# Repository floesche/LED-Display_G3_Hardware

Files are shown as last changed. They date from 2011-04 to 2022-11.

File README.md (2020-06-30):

# Modular display system, Generation 3 Hardware

This repository contains information related to the 3rd generation of modular
displays, as described in:

Reiser, M.B. and Dickinson, M.H., 2008. A modular display system for insect behavioral neuroscience. *Journal of Neuroscience Methods, 167*(2), pp.127-139 [doi:10.1016/j.jneumeth.2007.07.019](https://doi.org/10.1016/j.jneumeth.2007.07.019)

More information is available in the [Wiki](https://github.com/reiserlab/Panel-G3-Hardware/wiki)

This repository used to live on https://bitbucket.org/mreiser before June 2020.

## related repositories

- (this repository) [Panel Generation 3 Hardware](https://github.com/reiserlab/Panel-G3-Hardware)
- [Panel Generation 3 Software](https://github.com/reiserlab/Panel-G3-Software)
- [Panel Generation 4 Tools](https://github.com/JaneliaSciComp/G4_Display_Tools)

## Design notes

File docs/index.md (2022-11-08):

---
title: Hardware
parent: Generation 3
has_children: true
has_toc: false
nav_order: 1
---

# Home

These pages document the hardware details of the Generation 3 controller project (PDC 3.0, released April 2011). The documentation for the version 2 of the project is archived [here]({{site.baseurl}}/G2/).

What is new in PDC 3.0?

- Xmega controller
- 4 I²C busses
- improved ADC and DCA components

# At a Glance

1. The flight arena consists of a circular array of 8×8 dot matrix displays of LEDs with additional electronics to drive the display.
1. The data acquisition module is often called the NI-DAQ (National Instruments Data Acquisition Device). In this case, the NI-DAQ is a [NI USB-6229 BNC](https://www.ni.com/documentation/en/multifunction-io-device/latest/usb-6229/pinout-bnc/) Multifunction DAQ. This model has 16 analog inputs, 4 analog outputs, 8 DIOs and 2 user defined BNC terminals—more information about this device is available at <http://sine.ni.com/nips/cds/view/p/lang/en/nid/203866>.
1. The controller is a microprocessor circuit custom designed to operate the flight arena. The controller communicates with a PC through a serial port and to the panels using a rapid serial interface.
1. The wingbeat analyzer measures the frequency and amplitude of the fly wing stroke. It also computes the sum and difference of the amplitudes of the left and right wings. This device is custom built by JFI Electronics at the University of Chicago.
1. The PC is used to display patterns on the flight arena and record data through the NI-DAQ. The PC must be capable of running Matlab as well as a data acquisition program such as [AxoScope](https://www.moleculardevices.com/products/axon-patch-clamp-system/acquisition-and-analysis-software/pclamp-software-suite) or [Spikehound](https://sourceforge.net/projects/spikehound/). It must have at least one USB and one serial port.
1. An oscilloscope with three input channels and an external trigger will suffice.

# Required parts

The following is a brief list of the parts needed for a functional setup.

## Data Processing & Acquisition

1. Arena Controller -  (URL/controller details neeeded)
1. Wingbeat Analyzer (WBA) - [JFI Electronics Laboratory](https://jfi.uchicago.edu/), University of Chicago.
1. Data Acquisition Module -  [National Instruments Data Acquisition PCI-6221 Board (NI-DAQ)](http://sine.ni.com/nips/cds/view/p/lang/en/nid/14132)
1. Oscilloscope - [Tektronix TDS 2024B](https://www.tek.com/oscilloscope/tds2000-digital-storage-oscilloscope)
1. PC - Any PC capable of running matlab, a data acquisition program, and handling the card drivers for the NI-DAQ. - Our setup uses Dell Precision T5500
1. Cables - BNC, BNC-Banana adaptors, BNC T splitters, FireWire, USB A-B

## Flight Arena & Peripherals

(See [Arenas Page](g3_arenas.md) for assembly information)

1. [LED Display Panels](assets/green-panels_BM-10288MD.pdf)
1. Arena Boards - (needed)
1. IR Sensor/Cover - (needed)
1. IR Diode - (needed)
1. Camera - Point Gray Research [Firefly](http://www.ptgrey.com/products/fireflymv/fireflymv_usb_firewire_cmos_camera.asp)
1. Stage - [Thorlabs](http://www.thorlabs.com) components
1. Enclosure - Any material capable of covering the arena and preventing light from entering.
1. SDHC/CF Card - Such as from [Transcend](http://ec.transcendusa.com/product/product_memory.asp?Cid=92)

## Software

1. [MATLAB](http://www.mathworks.com/products/matlab/)
1. Data Acquisition - Such as [Spikehound](https://sourceforge.net/projects/spikehound/) or the Matlab Data Acquisition Toolbox

## Optional

1. Speakers - To hear the WBA
1. 80mm PC Case Fan - To encourage fly flight
1. Thermometer - For temperature sensitive experiments/consistency

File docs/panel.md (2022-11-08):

---
title: Panel
parent: Hardware
grand_parent: Generation 3
nav_order: 1
---

# Panel

The Generation 3 Modular LED Display uses the same panels as [Generation 2]({{site.baseurl}}/G2/). [See there]({{site.baseurl}}/Generation%202/Panels/docs/) for more information.

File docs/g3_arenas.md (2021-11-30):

---
title: Arenas
parent: Hardware
grand_parent: Generation 3
nav_order: 5
---

# Generation 3 Arena

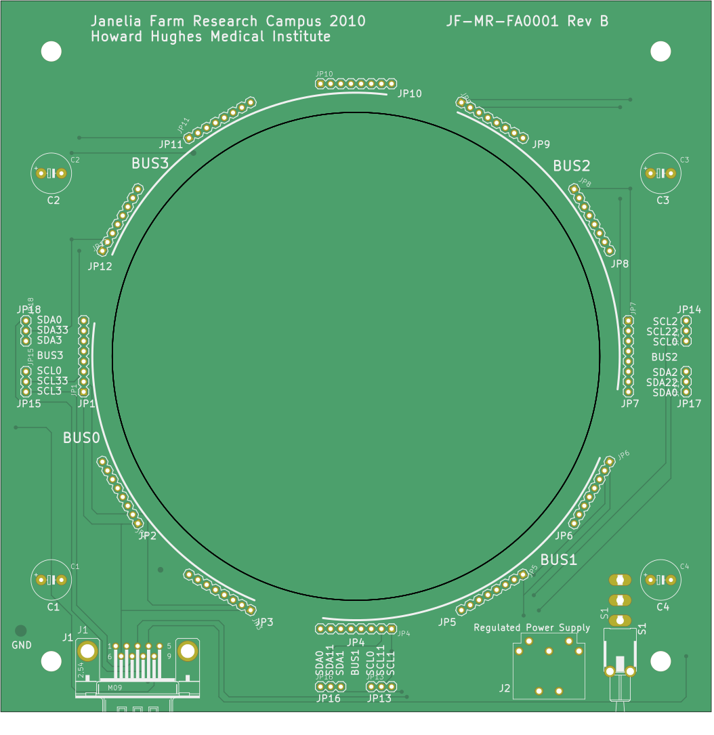
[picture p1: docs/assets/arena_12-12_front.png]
Arena 12-12 PCB front view

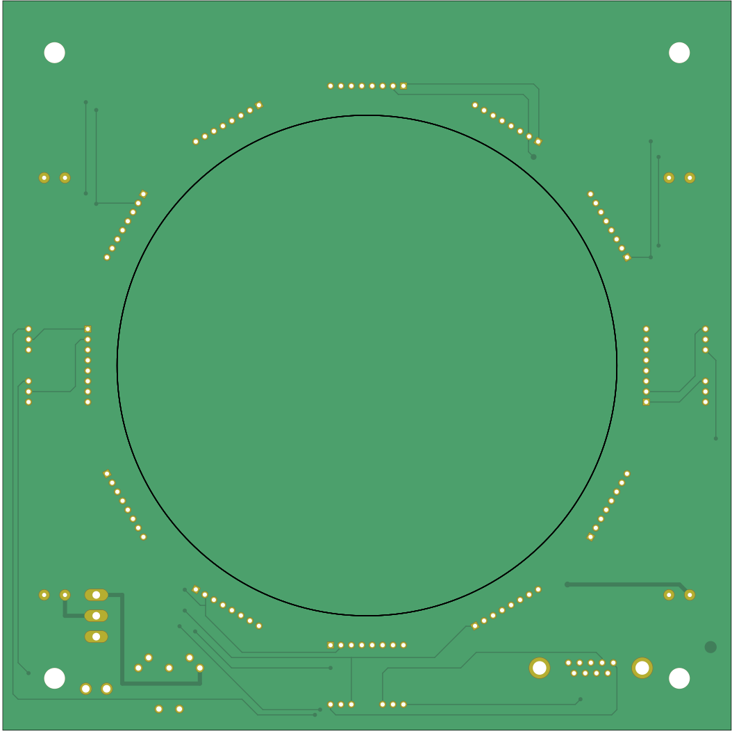
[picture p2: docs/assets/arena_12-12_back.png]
Arena 12-12 PCB back view


An arena board organizes panels in a geometry and provides structural integrity to the whole setup. Different shapes of cylindrical arenas have been built. We use a naming scheme based on their number of panel columns available and the virtual ones forming a full circle. A 12-12 arena is a closed cylinder formed by 12 columns in total, a 12-20 describes an open virtual cylinder formed by 20 columns where 12 are actually available.

For the Generation 3, two different arenas are available: an arena 12-12 and arena 24-24. Besides the eagle project files, we provide a preview of the [schematics for the arena 12-12](assets/arena_12-12_schematic.pdf) and the most recent production files archived in `arena_12-12/production_v1/JF-MR-FA0001-RevB.zip`. The same applies to the [schematics](assets/arena_24-24_schematic.pdf) of the arena 24-24 with production files archived at `arena_24-24/production_v1/JF-MR-FA0002-RevA.zip`.

# Recommended method for assembling arenas

## Assembling the LED matrix

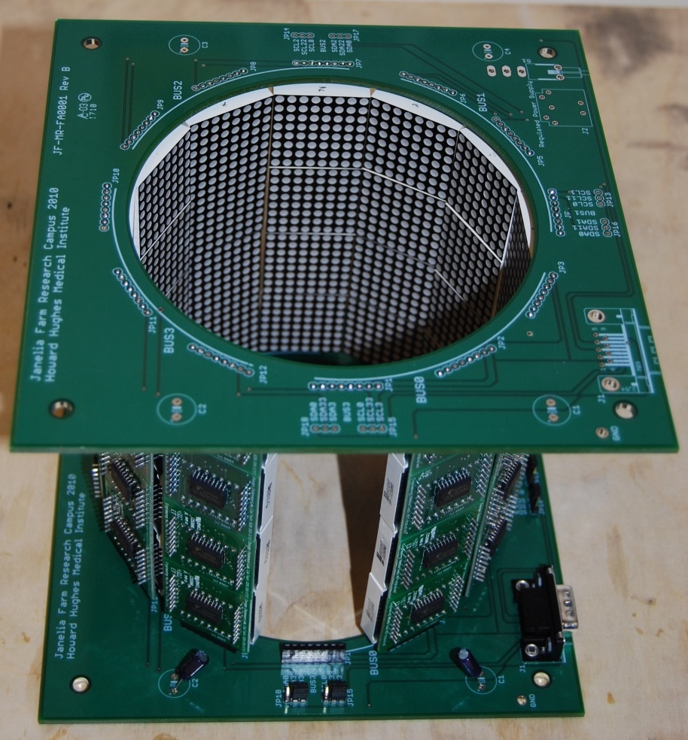
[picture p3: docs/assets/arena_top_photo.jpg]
An assembled arena - top view


The standard arena consists of a circular array of 8×8 dot matrix displays of LEDs connected to microcontrollers in a 1:1 manner. The typical 12 panel ring arena is built from two PCB boards, and is typically 4 panels high (48 panels total). In order to later control the displays, unique addresses must be assigned to each one. These micro controllers may need to be flashed with the latest files according to the [flash firmware guide]({{site.baseurl}}/Generation%203/Software/docs/g3_flash_firmware.html) before assigning addresses The following outlines the steps needed for creating a standard arena with a 4×11 array of LED displays.

1. Press each LED display into the microcontroller using the correct orientation. With the male side of the controller pointing down, the ink stamp of the LED should be on the right hand side before inserting pins.
1. Once 44 microcontroller/LED units have been assembled (or more, if some microcontrollers are not functioning), they must first be programmed and assigned addresses as outlined in the [flash firmware guide]({{site.baseurl}}/Generation%203/Software/docs/g3_flash_firmware.html).
    1. If the LED does not properly display lights, or is very dim compared to the rest, do not use it in your arena.
1. Connect each column to form the 12 columns of the matrix above. This will probably require partially pulling out the LED portion of each unit, connecting the male and female ends, and then securing the LED to the microcontroller once the connection is snug. (Note this problem may make itself more apparent when viewing the assembled columns, and fixing it will ensure strong electrical connections between units).

## Assembling the boards

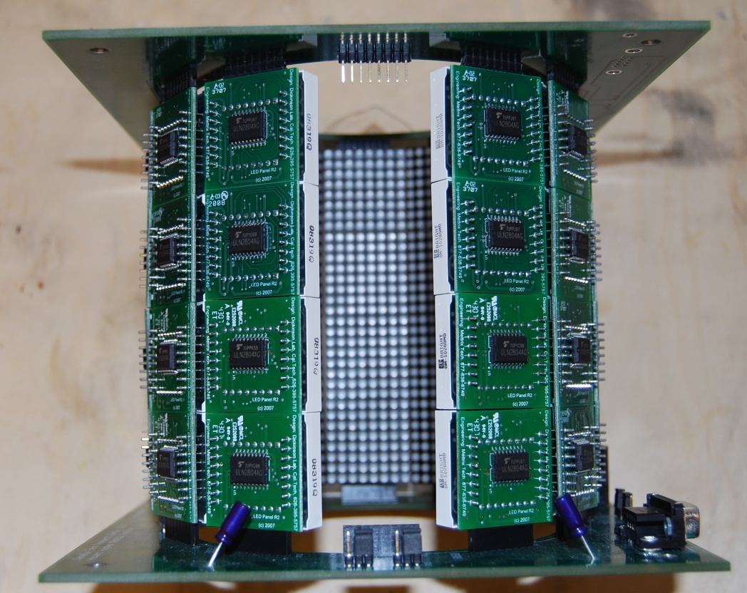
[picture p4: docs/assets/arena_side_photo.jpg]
An assembled arena - side view


The PCB boards for each arena require some soldering. Remember both boards must be facing up in the final arena, attach components on the correct side.

1. Bottom board (female end) requires 12, 8-pin stacking headers soldered around the center top (silkscreen text) circle cutout  side of the board.
1. Bottom board requires 4 capacitors, one in each corner of the board, with the correct polar orientation (see board, light stripe to the left).
1. Bottom board also requires a power supply input, jumpering pins, a switch, serial port, and switch to be securely soldered.
1. The top PCB should have male headers soldered to the bottom side (opposite the silkscreen text) that fit into the connectors of the top panels (additional components are not required on the top PCB, but capacitors are always a good idea).
1. Connect the LED columns to the bottom, then top boards.
1. Check that the panels turn on and are in the correct place by plugging in the 5V power supply and turning on the arena with the power switch.
1. Check for gaps between LED panels which can compromise the long term stability of the arena.

## Constructing the Arena Housing

Our lab uses supplies from [Thorlabs](http://www.thorlabs.com/) to construct a holder for the arena, IR diode, IR sensor, tether post, and camera. This can be accomplished with any sturdy materials, although Thor components are recommended because of their high modularity and strength (and lab snacks). Instead of giving exact directions, some required specifications will be listed.

1. The IR diode must be positioned pointing directly down on the center of the arena.
1. The IR sensor must be positioned directly under the center of the arena.
1. The tether post must end in the exact center of the arena with the fly between the IR diode and sensor, and at an 20-35 degree angle to the perpendicular.
1. The most useful placement of a camera is level with the fly for alignment purposes.

## Connecting Components

The assembled arena and remaining components must be properly connected using mainly BNC, USB and Serial Port connectors. When setting up the rest of the system, place all components in a user friendly arrangement (i.e. oscilloscope and analog camera output easily viewable). The following is a table, then diagram of connectivity. For more information on how each component works, see the [Flight Simulator User Guide]({{site.baseurl}}/Generation%202/Arenas/docs/g2_user-guide.html)  by Frye, Reiser, and Dickinson or read the Panels documentation page.

The following is a list of Components and connections. For example, the first line reads: the controller's `ADCO` is connected to the Wing beat analyzer's WBA input

| Component side A | Connection side A | Component side B  | Connection side B |
| ---------------- | ----------------- | ----------------- | ----------------- |
| Controller       | ADC0              | Wingbeat Analyzer | L                 |
| Controller       | ADC1              | Wingbeat Analyzer | R                 |
| Controller       | DAC0              | NI-DAQ            | Input 3           |
| Controller       | DAC1              | NI-DAQ            | Input 4           |
| Controller       | PC1               | Computer          | Serial Port       |
| Controller       | I2C               | Arena             | Serial Port       |
| NI-DAQ           | Analog Input 0    | Wingbeat Analyzer | Amplitude L       |
| NI-DAQ           | Analog Input 1    | Wingbeat Analyzer | Amplitude R       |
| NI-DAQ           | Analog Input 2    | Wingbeat Analyzer | Frequency         |
| NI-DAQ           | Analog Input 3    | Controller        | DAQ1              |
| NI-DAQ           | Analog Input 4    | Controller        | DAQ2              |
| NI-DAQ           | Analog Input 5    | Wingbeat Analyzer | Amplitude L-R     |
| NI-DAQ           | Analog Input 6    |                   | Analog Output 1   |
| NI-DAQ           | USB Output        | Computer          | USB-Port          |
| NI-DAQ           | Analog Output 1   |                   | Analog Input 6    |
| Wingbeat Analyzer| L                 | Controller        | ADC0              |
| Wingbeat Analyzer| L                 | NI-DAQ            | Analog Input 0    |
| Wingbeat Analyzer| R                 | Controller        | ADC1              |
| Wingbeat Analyzer| R                 | NI-DAQ            | Analog Input 1    |
| Wingbeat Analyzer| Signal Out L + R  | Oscilloscope      | Ch 1 + Ch 2       |
| Wingbeat Analyzer| Signal Out L + R  | Speakers          | L + R             |
| Wingbeat Analyzer| L-R               | Oscilloscope      | Ch 3              |
| Wingbeat Analyzer| L-R               | NI-DAQ             | Analog Input 5    |
| Wingbeat Analyzer| SYNC (-TTL)       | Oscilloscope      | Ext Trig          |
| Wingbeat Analyzer| LED Out           | Arena             | IR LED            |
| Wingbeat Analyzer| Photo detector    | Arena             | Photo detector    |
| Wingbeat Analyzer| Frequency         | NI-DAQ            | Analog Input 2    |
| Oscilloscope     | Channel 1         | Wingbeat Analyzer | L                 |
| Oscilloscope     | Channel 2         | Wingbeat Analyzer | R                 |
| Oscilloscope     | Channel 3         | Wingbeat Analyzer | L-R               |
| Oscilloscope     | Ext Trig          | Wingbeat Analyzer | SYNC (-TTL)       |
| Arena            | Serial Port       | Controller        | I2C               |
| Arena            | Photodetector     | Wingbeat Analyzer | Photodetector     |
| Arena            | LED               | Wingbeat Analyzer | LED Out           |
| Computer         | USB               | NI-DAQ            |                   |
| Computer         | Serial Port       | Controller        | PC1               |

# Power issues

(needed)

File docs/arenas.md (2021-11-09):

---
title: Arenas
parent: Hardware
grand_parent: Generation 3
nav_order: 3
---

# Recommended method for assembling arenas

## Assembling the LED matrix

The standard arena consists of a circular array of 8×8 dot matrix displays of LEDs connected to microcontrollers in a 1:1 manner. The typical 12 panel ring arena is built from two PCB boards, and is typically 4 panels high (48 panels total). In order to later control the displays, unique addresses must be assigned to each one. These micro controllers may need to be flashed with the latest files according to the [quick start guide]({{site.baseurl}}/Generation%203/Software/docs/quick-start.html) before assigning addresses The following outlines the steps needed for creating a standard arena with a 4×11 array of LED displays.

1. Press each LED display into the microcontroller using the correct orientation. With the male side of the controller pointing down, the ink stamp of the LED should be on the right hand side before inserting pins.
1. Once 44 microcontroller/LED units have been assembled (or more, if some microcontrollers are not functioning), they must first be programmed and assigned addresses as outlined in the [Quick Start guide]({{site.baseurl}}/Generation%203/Software/docs/quick-start.html).
    1. If the LED does not properly display lights, or is very dim compared to the rest, do not use it in your arena.
1. Connect each column to form the 12 columns of the matrix above. This will probably require partially pulling out the LED portion of each unit, connecting the male and female ends, and then securing the LED to the microcontroller once the connection is snug. (Note this problem may make itself more apparent when viewing the assembled columns, and fixing it will ensure strong electrical connections between units).

## Assembling the boards

The PCB boards for each arena require some soldering. Remember both boards must be facing up in the final arena, attach components on the correct side.

1. Bottom board (female end) requires 12, 8-pin stacking headers soldered around the center top (silkscreen text) circle cutout  side of the board.
1. Bottom board requires 4 capacitors, one in each corner of the board, with the correct polar orientation (see board, light stripe to the left).
1. Bottom board also requires a power supply input, jumpering pins, a switch, serial port, and switch to be securely soldered.
1. The top PCB should have male headers soldered to the bottom side (opposite the silkscreen text) that fit into the connectors of the top panels (additional components are not required on the top PCB, but capacitors are always a good idea).
1. Connect the LED columns to the bottom, then top boards.
1. Check that the panels turn on and are in the correct place by plugging in the 5V power supply and turning on the arena with the power switch.
1. Check for gaps between LED panels which can compromise the long term stability of the arena.

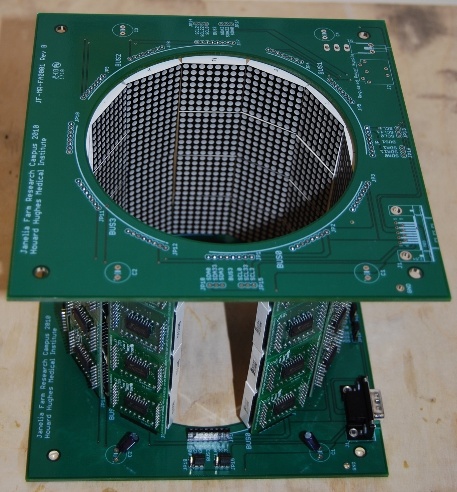
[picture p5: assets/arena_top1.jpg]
An assembled arena - top view

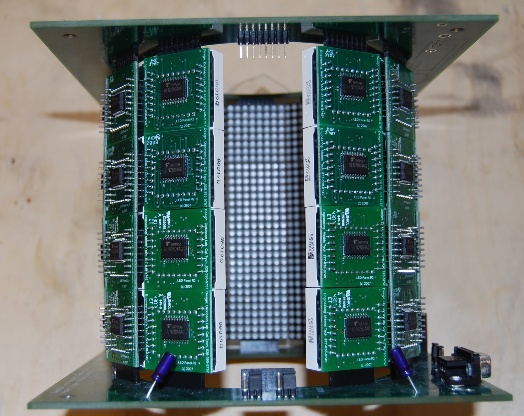
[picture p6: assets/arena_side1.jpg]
An assembled arena - side view


---
{:.clear}

## Constructing the Arena Housing

Our lab uses supplies from [Thorlabs](http://www.thorlabs.com/) to construct a holder for the arena, IR diode, IR sensor, tether post, and camera. This can be accomplished with any sturdy materials, although Thor components are recommended because of their high modularity and strength (and lab snacks). Instead of giving exact directions, some required specifications will be listed.

1. The IR diode must be positioned pointing directly down on the center of the arena.
1. The IR sensor must be positioned directly under the center of the arena.
1. The tether post must end in the exact center of the arena with the fly between the IR diode and sensor, and at an 20-35 degree angle to the perpendicular.
1. The most useful placement of a camera is level with the fly for alignment purposes.

## Connecting Components

The assembled arena and remaining components must be properly connected using mainly BNC, USB and Serial Port connectors. When setting up the rest of the system, place all components in a user friendly arrangement (i.e. oscilloscope and analog camera output easily viewable). The following is a table, then diagram of connectivity. For more information on how each component works, see the [Flight Simulator User Guide]({{site.baseurl}}/Generation%203/Software/docs/g2-user-guide.html)  by Frye, Reiser, and Dickinson or read the Panels documentation page.

The following is a list of Components and connections. For example, the first line reads: the controller's ADCO is connected to the Wing beat analyzer's WBA input

| Component side A | Connection side A | Component side B  | Connection side B |
| ---------------- | ----------------- | ----------------- | ----------------- |
| Controller       | ADC0              | Wingbeat Analyzer | L                 |
| Controller       | ADC1              | Wingbeat Analyzer | R                 |
| Controller       | DAC0              | NI-DAQ            | Input 3           |
| Controller       | DAC1              | NI-DAQ            | Input 4           |
| Controller       | PC1               | Computer          | Serial Port       |
| Controller       | I2C               | Arena             | Serial Port       |
| NI-DAQ           | Analog Input 0    | Wingbeat Analyzer | Amplitude L       |
| NI-DAQ           | Analog Input 1    | Wingbeat Analyzer | Amplitude R       |
| NI-DAQ           | Analog Input 2    | Wingbeat Analyzer | Frequency         |
| NI-DAQ           | Analog Input 3    | Controller        | DAQ1              |
| NI-DAQ           | Analog Input 4    | Controller        | DAQ2              |
| NI-DAQ           | Analog Input 5    | Wingbeat Analyzer | Amplitude L-R     |
| NI-DAQ           | Analog Input 6    |                   | Analog Output 1   |
| NI-DAQ           | USB Output        | Computer          | USB-Port          |
| NI-DAQ           | Analog Output 1   |                   | Analog Input 6    |
| Wingbeat Analyzer| L                 | Controller        | ADC0              |
| Wingbeat Analyzer| L                 | NI-DAQ            | Analog Input 0    |
| Wingbeat Analyzer| R                 | Controller        | ADC1              |
| Wingbeat Analyzer| R                 | NI-DAQ            | Analog Input 1    |
| Wingbeat Analyzer| Signal Out L + R  | Oscilloscope      | Ch 1 + Ch 2       |
| Wingbeat Analyzer| Signal Out L + R  | Speakers          | L + R             |
| Wingbeat Analyzer| L-R               | Oscilloscope      | Ch 3              |
| Wingbeat Analyzer| L-R               | NI-DAQ             | Analog Input 5    |
| Wingbeat Analyzer| SYNC (-TTL)       | Oscilloscope      | Ext Trig          |
| Wingbeat Analyzer| LED Out           | Arena             | IR LED            |
| Wingbeat Analyzer| Photo detector    | Arena             | Photo detector    |
| Wingbeat Analyzer| Frequency         | NI-DAQ            | Analog Input 2    |
| Oscilloscope     | Channel 1         | Wingbeat Analyzer | L                 |
| Oscilloscope     | Channel 2         | Wingbeat Analyzer | R                 |
| Oscilloscope     | Channel 3         | Wingbeat Analyzer | L-R               |
| Oscilloscope     | Ext Trig          | Wingbeat Analyzer | SYNC (-TTL)       |
| Arena            | Serial Port       | Controller        | I2C               |
| Arena            | Photodetector     | Wingbeat Analyzer | Photodetector     |
| Arena            | LED               | Wingbeat Analyzer | LED Out           |
| Computer         | USB               | NI-DAQ            |                   |
| Computer         | Serial Port       | Controller        | PC1               |

# Power issues

(needed)

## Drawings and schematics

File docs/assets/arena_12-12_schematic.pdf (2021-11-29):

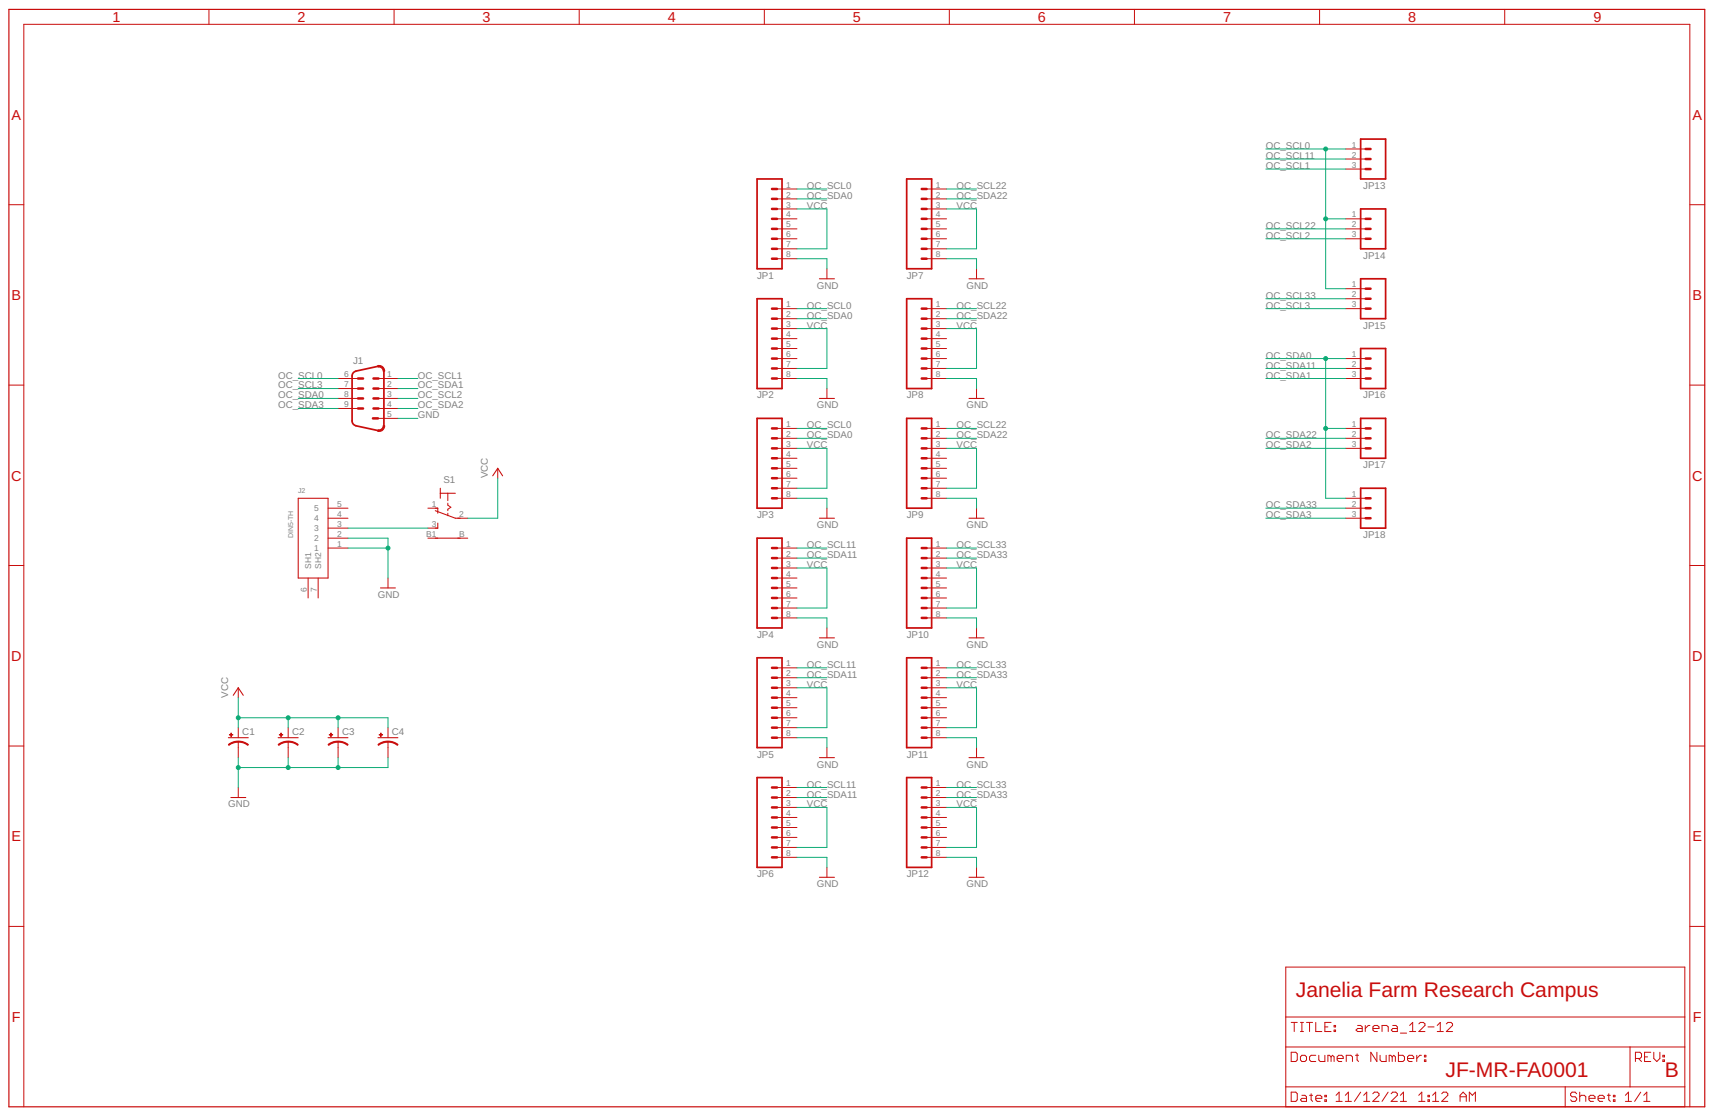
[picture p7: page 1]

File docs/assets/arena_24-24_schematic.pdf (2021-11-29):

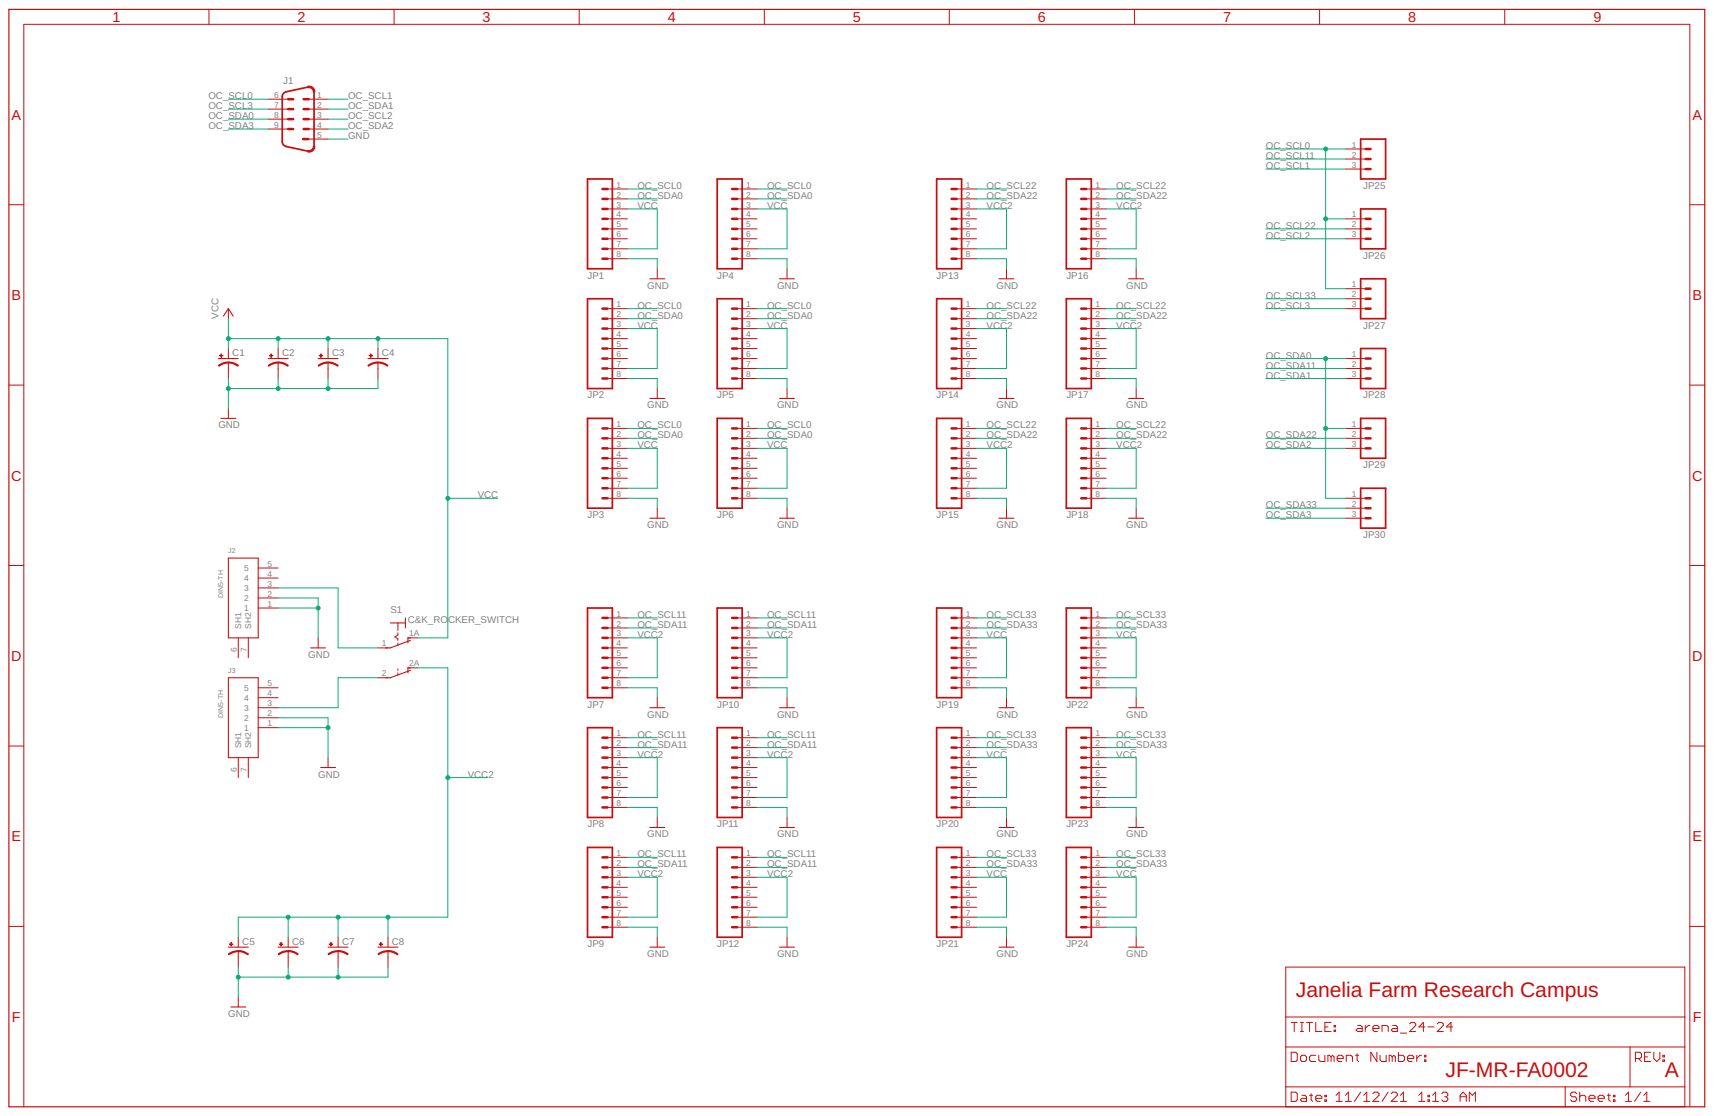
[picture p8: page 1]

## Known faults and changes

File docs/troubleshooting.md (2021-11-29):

---
title: Troubleshooting
parent: Hardware
grand_parent: Generation 3
nav_order: 6
---

# Tips & Tricks

The [Flight Arena User Guide]({{site.baseurl}}/Generation%202/Arenas/docs/g2_user-guide.html) has many suggestions for proper technique.

Some common problems that come up are:

## The Oscilloscope is not showing wing beat waveforms correctly

First make sure the fly is directly aligned under the IR LED and above the IR sensor, that the correct BNC cords are plugged in, and that they are the channels shown on the display. The settings commonly used per channel are:

1. 1V Vertical Scale
1. 2.5ms Horizontal Scale
1. DC coupling
1. Default (1×) probe voltage
1. Set the trigger to either of the channels with wing beat amplitude or use the TTL from the wingbeat analyzer

Depending on your model, you may need to invert the signals to show the traditional Hütchen shape.

If switching settings does not work, try to realign the fly again.

## A single panel not refreshing correctly

This means, it stays off, on, or static when a pattern is passed to the arena. If simply resetting the panel and controller do not fix the issue try the following list. A good way to check for functionality is asking the panel controller to display bus numbers (through PControl: *Panel*{:.gui-btn} → *Show Bus Number*{:.gui-btn}). If the panel does not update, try the following:

- Turning off the controller, and arena followed by a resetting of the panel, or jiggling in the top and bottom portions to make a snug connection and trying again.
- Reassigning the arena configuration. After placing an arena config file on an SD card using PControl: *Configurations*{:.gui-btn} → *load config to SD card*{:.gui-btn}, insert the SD card and set the new config (or old config if you are simply resetting it). To do this use PControl: *Configurations*{:.gui-btn} → *set arena config*{:.gui-btn}.
- If the above does not work, you may need to assemble, flash, and address a new panel.

## An entire column of panels is not turning on

The likely solution is a soldering issue, if you find the problem is limited to just the one column (i.e. not an issue with the panels) you may need to take the arena apart and re-solder the bottom and/or top PCB boards. Note that the arena does not require the top board to function, but it may aid in stability and establishing solid electrical connections.

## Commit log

2011-04-28 Added 12 and 24 panel arena design files. Modified directory structure somewhat. Renamed images.
    [Fly Arena Base-24.GBL, Fly Arena Base-24.GBS, Fly Arena Base-24.GTL, Fly Arena Base-24.GTO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]
2020-06-30 rename paths
    [Fly Arena Base-24.GBL, Fly Arena Base-24.GBS, Fly Arena Base-24.GTL, Fly Arena Base-24.GTO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]
2021-11-12 clean up arena
    [Fly Arena Base-24.GBL, Fly Arena Base-24.GBS, Fly Arena Base-24.GTL, Fly Arena Base-24.GTO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]
